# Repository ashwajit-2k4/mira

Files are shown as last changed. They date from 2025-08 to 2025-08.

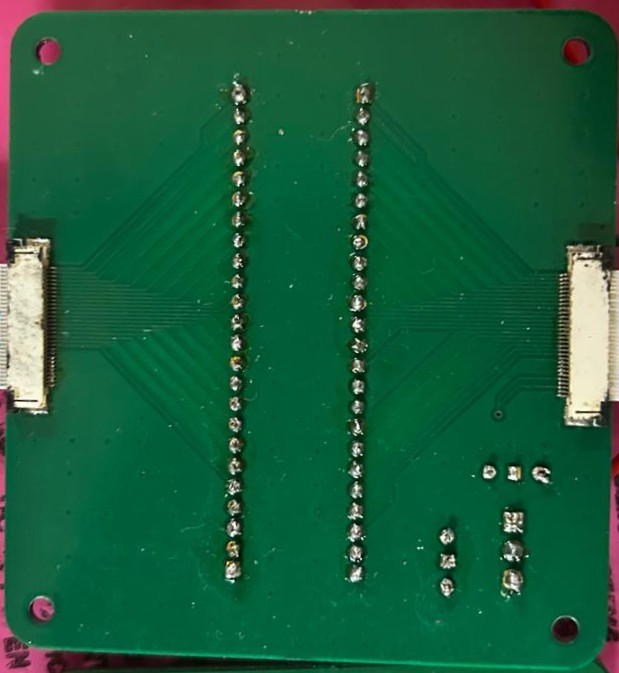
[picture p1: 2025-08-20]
pcb/PCB_2/pictures/CMOD_PCB_Back_Assembled.jpeg

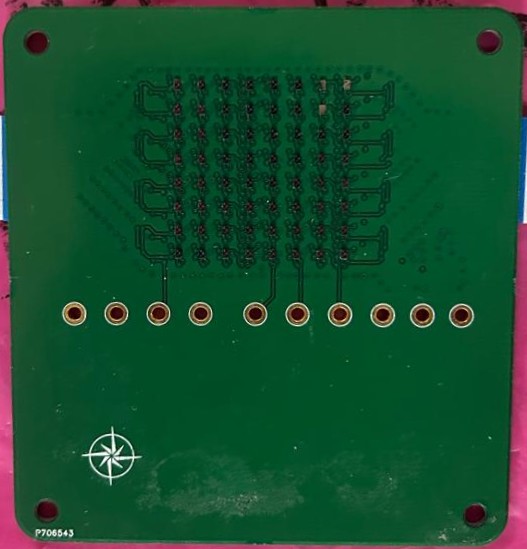
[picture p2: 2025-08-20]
pcb/PCB_1/pictures/EDL_3001_PCB_Back_Assembled.jpeg

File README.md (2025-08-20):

### EDL 2025 Project Submission Repository.

### Project Name: P-05 : Magnetic Field Camera
### Team Number: MON-08
### Team Members:
- Aditya Vema Reddy Kesari (22b3985)
- Ashwajit Singh (22b1227)
- N V Navaneeth Rajesh (22b1215)
- Raunak Mukherjee (22b3955)
- Suchet Gopal (22b1814)

### Problem Statement and Solution:

<!-- Provide a description about the project and what you've learnt and achieved in this. -->

<b> Problem Statement </b> 

High resolution magnetic imaging of objects is extremely important in industrial applications, to check for defects in manufactured parts like permanent magnets or motors. However, many current products like MAGCAM have exhorbitant costs that make them unviable for many people.

<b> Our Solution </b> 

MIRA M1 fills in this gap, as an affordable  magnetic field camera consisting of an 8x8 sensor array, that maps the field distribution in the volume around an object using an r-theta-z movement rig in just a few minutes. 

The object to be measured is placed on a rotating platform, with the sensor array itself moving in the r-z plane, thus enabling the mapping out of 3D space. The user interacts with a laptop-based GUI, to move the sensors to the starting position, and then start the pre-programmed sweep. The GUI then shows the live heatmap of the values the sensor array sees (at above 80 frames per second), along with a continuously updating scatter plot showing a 3D visualisation of the field.

<b> How It Works </b> 

The GUI starts an SSH connection to a Raspberry Pi, that controls the motors for rig movement, and communicates with the CMOD A7 FPGA that interfaces with the sensor array. When acquisition is started, the RPi rotates the theta motor by 360 degrees in 200 steps, acquiring data from sensors in every step. It then moves in the r direction in steps, repeating this process before it moves up in the z direction.

<b> Deliverables </b> 

- 2mm spatial resolution: **Achieved** (Currently with 1.75mm resolution, which can be increased further)
- 1mT sensitivity: **Achieved** (Obtained 0.2mT sensitivity)

### Key Learnings

Since our project had a lot of moving parts, with the CMOD FPGA, the Raspberry Pi microcontroller and the laptop GUI, in addition to the motor movement mechanism, communication was essential to ensure compatibility between these parts. Additionally, we had to put a lot of thought into component choice, since we could not use commonly available steel components due to interference. Since we required very high resolution, both in terms of magnetic field and spatial movement, it required careful design of PCBs and CAD models, and required adapting parts in the mechanism to ensure that we had minimum spatial error from jitter.

### Walkthrough of the repo

The source code consists of code for 3 devices: CMOD A7 FPGA, Raspberry Pi 5 and the laptop GUI. Additionally, the PCB designs for the sensor PCB we ultimately used, along with the backup PCB, and the PCB containing the FPGA are provided. The CAD models for all 3D printed and laser cut parts are also provided.

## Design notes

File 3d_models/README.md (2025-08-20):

# 3D Models

The project consists of several parts listed below. For further details please refer to the individual folders

1. **Large Spacer**: This design is used to hold the PCBs in place, connect to the sensor head and provide a point to attach the acrylic shields to protect the PCBs.

2. **Motor enclosure**: This holds the motor controlling the theta DOF (through the platform) using the 3D printed holder, and the motor bracket to attach the motor for controlling the radial DOF.

3. **Slider**: This part holds the entire z-axis movement mechanism. It slides along the radial direction, moving the entire sensor head, and holds the motor to move in the z direction.

4. **Sensor Head**: This holds the sensor and CMOD PCBs via the large spacer, and is connected to the threaded rod and the support rod controlling the z axis.

5. **CMOD Acrylic Shield**: This attaches to the large spacer and provides an enclosure for the CMOD board.

6. **Sensor PCB Shield**: This acrylic part provides an enclosure for the sensor PCB, and attaches to the large spacer.

7. **Small Spacer**: This part helps provide separation between the PCBs.

8. **Support Rod Holder**: This part simply holds the two horizontal support rods in place, and provides support to the other end of the threaded rod in the r-axis.

9. **Secondary Support Rod Holder**: This part holds only the support rods in place, with space in the middle to allow the motor shaft, coupler and threaded rod the pass through.

10. **Platform**: The object to be characterised is placed on this rotating platform.

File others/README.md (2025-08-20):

## Overview

The `others/` folder contains supplementary resources related to the final hardware assembly, usage, and documentation.

### Folder Structure

- **`PCBs/`**  
  Includes images of the fully assembled and soldered PCBs, along with a block diagram illustrating their interconnection and function in the system.

- **`Motors/`**  
  Contains photos of the perf board used for the motor driver circuit, including components and wiring.

- **`User Manual/`**  
  Provides a guide on how to use the project, including setup instructions, system overview, and basic operational steps.

---

These files serve as a reference for understanding the hardware integration and for guiding users on how to operate the magnetic field camera system.

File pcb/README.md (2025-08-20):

# PCB Overview

This folder contains all the design files, layouts, schematics, and assembled images for the PCBs developed for our project.

## PCB Summary

| PCB | Description | 
|-----|-------------|
| **PCB_1** | `TMAG3001 Sensor Array` – An 8×8 array using I2C-based TMAG3001 magnetometers. Used in the final sensor head. | 
| **PCB_2** | `CMOD Interface Board` – Interfaces the TMAG sensor array (PCB_1 or PCB_3) with a CMOD FPGA module. Includes power control and signal routing. | 
| **PCB_3** | `TMAG5170 Sensor Array` – A backup 8×8 sensor array using SPI-based TMAG5170 magnetometers. Fully compatible with PCB_2. | 

---

## Sensor Head Configuration

The **sensor head** for the magnetic field camera is built using:
- **PCB_2** (CMOD Interface)
- **Either** PCB_1 **or** PCB_3 (Sensor Array)

> Note: PCB_3 serves as an alternative to PCB_1 and can be used interchangeably without any hardware modifications.

---

## Manufacturing Note

Due to the complexity and design constraints, **none of the PCBs could be fabricated in-house at IIT Bombay**.  
All boards were professionally manufactured by **PCB Power**.

---

## Folder Contents

Each PCB folder contains:
- **Schematics**
- **PCB Layouts**
- **3D Renders**
- **Assembled Board Images**

---

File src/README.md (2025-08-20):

## Overview

This folder contains the complete codebase for the project, divided into three main components based on the hardware platform they run on:

### CMOD (FPGA)
- **Platform:** CMOD FPGA (e.g., CMOD A7)
- **Function:** Collects data from the TMAG sensor array and relays it to the Raspberry Pi via SPI.

### Raspberry Pi 5
- **Platform:** Raspberry Pi 5
- **Functions:**
  - Controls the motors and manages the motion of the sensor rig.
  - Receives sensor data from the FPGA and transmits it to the Laptop.

### Laptop
- **Platform:** PC or Laptop
- **Function:** Acts as the GUI for the project, providing visualization and user controls.

---

Each subfolder contains a more detailed description of the code and instructions on how to run it.

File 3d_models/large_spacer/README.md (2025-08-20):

# Large Spacer

## Purpose

This design is used to hold the PCBs in place, connect to the sensor head and provide a point to attach the acrylic shields to protect the PCBs.

##  Description

- **Type:** 3D print
- **Material Suggested:** PLA
- **Approx. Size:** 79mm x 80mm x 32mm

## Assembly Instructions

1. The two acrylic shields for the PCBs attach to either side of the part.
2. The PCBs are placed in between, with the extra space on one side for attaching to the sensor head
3. There are 4 3.2mm screw holes to attach parts together.
4. Please refer to the overall assembly image for reference

## Notes

A suggestion for future versions of this is to increase the clearance from the PCBs above, to allow space for the ribbon cables.

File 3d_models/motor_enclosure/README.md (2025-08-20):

# Motor Enclosure

## Purpose

This holds the motor controlling the theta DOF (through the platform) using the 3D printed holder, and the motor bracket to attach the motor for controlling the radial DOF.

##  Description

- **Type:** 3D print
- **Material Suggested:** PLA
- **Approx. Size:** 61mm x 57mm x 71mm

## Assembly Instructions

1. The 3D printed holder at the top allows the motor to be placed directly inside (an adhesive could be used for futher securing it)
2. The motor bracket is placed inside the enclosure, with the two slots fitting in. The motor is then screwed into it.

## Notes

The motors ran very hot, causing some bending in the plastic. A heat sink or a different material might be helpful.

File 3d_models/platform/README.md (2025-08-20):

# Platform

## Purpose

The object to be characterised is placed on this rotating platform.

##  Description

- **Type:** 3D print
- **Material Suggested:** PLA
- **Approx. Size:** 80mm x 80mm x 40mm
  
## Assembly Instructions

1. The 8mm shaft of the platform is inserted in the NEMA17 coupler, which in turn is connected to the motor controlling the theta DOF.

## Notes

A lnoger shaft for this piece would be better in a v2, since attaching it to the coupler was a struggle.

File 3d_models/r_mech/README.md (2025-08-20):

# Slider

## Purpose

This part holds the entire z-axis movement mechanism. It slides along the radial direction, moving the entire sensor head, and holds the motor to move in the z direction.

##  Description

- **Type:** 3D print
- **Material Suggested:** PLA
- **Approx. Size:** 65mm x 90mm x 50mm

## Assembly Instructions

1. 4 linear bearings are placed in the two holes on either side to run the support rods through
2. The flange nut is placed in the cavity in the centre hole, and a threaded rod is run through it
3. The motor controlling the z-axis is placed in the holder on top

## Notes

A suggestion for future versions of this is to increase the clearance from the PCBs above, to allow space for the ribbon cables.

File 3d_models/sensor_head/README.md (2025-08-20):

# Sensor Head

## Purpose

This holds the sensor and CMOD PCBs via the large spacer, and is connected to the threaded rod and the support rod controlling the z axis.

##  Description

- **Type:** 3D print
- **Material Suggested:** PLA
- **Approx. Size:** 40mm x 75mm x 70mm
  
## Assembly Instructions

1. 2 linear bearings are inserted in the 12mm hole to run the support rod through it.
2. The flange nut is inserted in the space provided with the screw holes, and the threaded rod is run through it.
3. This part is screwed to the spacers and PCBs through the screw holes provided.

## Notes

An additional nut would probably help with stability, or alternatively an additional support rod.

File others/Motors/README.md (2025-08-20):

### Motor Driver Connections  

We make use of 3 NEMA-17 stepper motors, one each for R, Theta and Z respectively. These are supplied power by the 12V SMPS (through the TB6600 motor drivers). The motor drivers make use of microstepping, and can be configured using the DIP Switches to change their current draw and microstep count.  

Since the motor driver inputs are differential, we connect one of +/- to GND and the other to a GPIO Pin of the RPi 5.

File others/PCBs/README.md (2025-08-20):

### PCB Descriptions  

The CMOD Interface PCB is connected the sensors by the means of 2x 30 pin FPC 0.5mm pitch connnectors, one on each side of the board respectively.  
The backside of the CMOD PCB faces the backside of the TMAG3001 PCB (i.e., the side with pullups and decoupling caps).   

The Screw terminal on the CMOD PCB is meant for power delivery to the CMOD via the 5V connection - this results in a current draw of < 100 mA in active mode. The 3.3V connection supplies the sensors and has a power draw of ~ 200 mA in active mode, ~ 23 mA in idle mode. The PMOD header connects the CMOD to the master readout device (in our case, an RPi 5).

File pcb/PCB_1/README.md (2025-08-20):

# TMAG3001 Sensor Array PCB

This repository contains the design files and documentation for the **TMAG3001 Sensor Array PCB**. This is the **main PCB** of the project, designed for high-resolution magnetic field sensing using a dense grid of magnetometers.

## Overview

- **Sensor Type**: TMAG3001 3-axis magnetometers  
- **Array Size**: 8x8 grid (64 sensors)  
- **Inter-sensor Spacing**: 3.5 mm  
- **PCB Type**: 4-layer board  
- **Communication Protocol**: I2C  

---

## Design Details

### I2C Bus Structure

Each group of **4 sensors** forms a **single I2C bus**.  
- Each **TMAG3001** uses **3 I2C lines**: `SCL`, `SDA`, and `INT`.
- A single bus handles 4 sensors, with address selection via the `ADD` pin.
- The `ADD` pin is tied to one of: `VCC`, `GND`, `SCL`, or `SDA` — enabling 4 unique addresses per bus.

> **Note**: To reduce the number of GPIOs, the `INT` lines from every **2 buses are shorted** together.

### Electrical Components

- **Pull-up Resistors**: 1.8 kΩ on all I2C lines  
- **Decoupling Capacitors**:
  - 0.1 µF per IC
  - 2 × 1 µF bulk capacitors at the power input  
- **Power Supply Pins** (per IC): `VCC`, `GND`, `INT`, `SCL`, `SDA`, `ADD`

### Physical Layout

- **IC Placement**: Only TMAG3001 ICs are placed on the **top** layer to avoid magnetic interference.
- **Other Components**: All resistors, capacitors, connectors, etc., are placed on the **bottom** layer.
- **Test Points**: 10 test points on the **bottom** for signal probing and ground testing.

### Grounding and Layer Design

- All 4 layers have **solid ground pours** for noise suppression and signal integrity.

---

## Files & Resources

The repository folders include:
- **Schematic**
- **PCB Layout**
- **3D Renders**
- **Assembled PCB Images**

---

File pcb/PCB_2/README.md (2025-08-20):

# CMOD Interface PCB

This PCB is designed to work in conjunction with the **TMAG3001 Sensor Array PCB**, forming a complete sensor head system. It serves as the interface between the microcontroller and the sensor array.

## Overview

- **Purpose**: Interface the TMAG3001 sensor array with a CMOD FPGA module  
- **CMOD Support**: Two sets of pin headers to securely mount the CMOD  
- **Signal Routing**: All signals are routed via ribbon cable connectors coming from the TMAG3001 Sensor Array PCB  
- **Power Supply**:  
  - Screw terminal block for providing power to both the FPGA and the sensor array  
  - Switches included to control the power supply to different sections

---

## Features

- **Ribbon Cable Connectors**:  
  - Located on both edges of the PCB  
  - Carry all signal lines from the sensor array PCB  

- **Power Interface**:  
  - Screw terminal for 3.3V/5V input  
  - Power control switches to selectively enable/disable supply to the FPGA and sensor PCB  

- **Mechanical Support**:  
  - Dual header slots to mount a CMOD A7 or similar FPGA board securely

---

## Files & Resources

The repository folders include:
- **Schematic**
- **PCB Layout**
- **3D Renders**
- **Assembled PCB Images**

---

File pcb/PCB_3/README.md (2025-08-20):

# TMAG5170 Sensor Array PCB

This PCB serves as a **backup** to the main TMAG3001-based board, utilizing **TMAG5170** sensors to form an 8×8 magnetometer array. It is a **2-layer** board designed for ease of hand assembly and SPI-based communication.

## Overview

- **Sensor Type**: TMAG5170 3-axis magnetometers  
- **Array Size**: 8×8 grid (64 sensors)  
- **Inter-sensor Spacing**: 4.625 mm  
- **PCB Type**: 2-layer board  
- **Communication Protocol**: SPI  

---

## Design Details

### SPI Bus Structure

Each **bus** handles 8 sensors (as seen in the schematic).  
- Required lines per bus: `INT`, `SCLK`, `MOSI`, `MISO`  
- Compatible with the same CMOD PCB interface used by the TMAG3001 board  
- Pins per TMAG5170 IC:
  - `VCC`, `GND`, `ALERT`, `SCLK`, `MOSI`, `MISO`, `TEST`, `CS`

> **Note**: Pin mapping ensures drop-in compatibility with existing CMOD interface hardware.

### Electrical Components

- **Pull-up Resistors**: 1.8 kΩ on all lines  
- **Decoupling Capacitors**:
  - 0.1 µF for each sensor IC  
  - 2 × 1 µF bulk capacitors at the input supply

### Physical Layout

- **IC Placement**: Only the TMAG5170 ICs are on the **front** of the PCB  
- **Other Components**: All resistors, capacitors, and connectors are on the **back**, minimizing interference during sensor operation   
- **Test Points**: 8 test points at the **bottom** of the PCB for signal and ground verification

### Assembly & Grounding

- Designed for **hand-soldering** – large enough component footprints  
- Both PCB layers are filled with **ground planes** for signal integrity

---

## Files & Resources

The repository folders include:
- **Schematic**
- **PCB Layout**
- **3D Renders**
- **Assembled PCB Images**

---

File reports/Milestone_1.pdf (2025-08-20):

# Project 5: Magnetic Field Camera

## MON-08

Aditya Vema
Ashwajit Singh
NV Navaneeth Rajesh
Raunak Mukherjee
Suchel Gopal

## Deliverable for Milestone 1

Please see forms that will be used for Milestone 1 evaluation. Two types of forms have to be filled out: 1. EE344_2025_milestone1 (1 form per team), 2. Individual_contribution_milestone1 (1 form per student)

You'll be asked to submit the following for Milestone 1 deadline (Feb 1st 2024):

1. PPT for Milestone 1, containing following information:
1. What is the problem that you are trying to solve?
2. Proposed solution, value proposition of your solution
3. How will you achieve the specifications? (i.e. overview of methodology, how did you arrive at the choice of solution after evaluating multiple options)
4. Technical details: principle of operation, target specifications, block diagram, justification of choice of components, BOM and accompanying circuit diagrams
5. Grant chart for project plan, work distribution across team members, week-wise goals
6. Key risks and mitigation strategies
7. Deliverables i.e. expected outcomes of the project
2. Video recording of PPT presentation (pre-recorded presentation. File size limit 100MB. Use Handbrake to compress video. Test your video and retake if needed)
3. BOM sheet (should be complete)
4. PDF of circuit diagrams of all blocks (as detailed as possible. BOM list should tally with circuit diagrams. Circuit diagrams may be hand-drawn using ruler and pen if that is more convenient and faster, but should be legible and all components should be clearly labeled.)

All the above deliverables have to be submitted for Milestone 1 deadline (Feb 1st 2024 - instructions and Google Form link will be shared)

## 01. Problem Statement

What is the problem we’re trying to solve?

- Quality control and manufacturing: Cracks, defects in permanent magnets used in motors, MRI machines
- Magnetic Shield Design and Testing: Helps design magnetic shields widely used in medical devices
- Medical Device Development: Testing implantable devices near magnets used in MRI machines
- Magnetic Levitation Systems: Testing bearings and components used in Maglev trains

## 02. Proposed Solution

What is the value proposition of our solution?
Millimeter precision and 3d interactive magnetic field visualisation to map the magnetic fields for crucial components in a short duration; enabling researchers to design and troubleshoot magnetic systems.

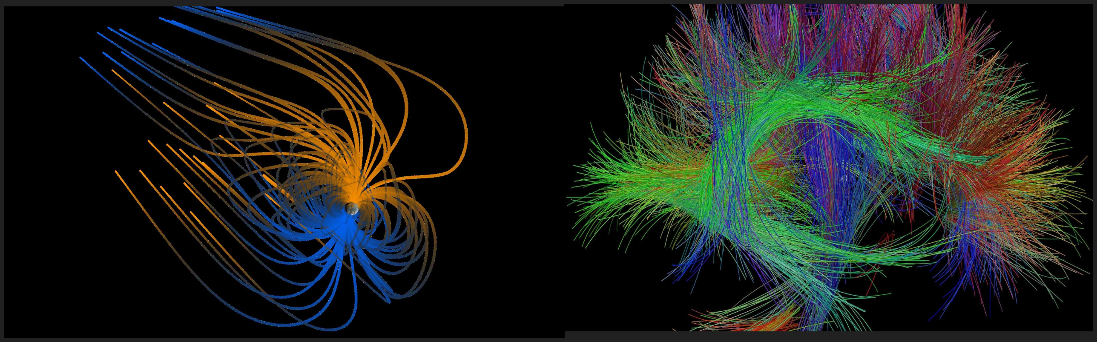
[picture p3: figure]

## 03. Achieving Specifications

How did we arrive at this solution after evaluating multiple options?

The alternatives have considerable drawbacks
1. Hand-held alternatives: Imprecise human operators require complicated sensors to detect position with no added benefit of precision
2. Magnetic Field with Real time Video: Real time video adds immense cost without the benefit of accuracy that is crucial to all conceivable applications.
3. Magnetic Field Cube: Our design facilitates 3 dof. We can thus repurpose several sensors to increase resolution in our measurement plane.
4. 2d field camera: Loses out crucial details present in the 3d magnetic field distribution

## 04. Technical Details

A. Principle of Operation
An 8x8 array of magnetic field sensors is mounted on an arm that moves cylindrically around an object and senses the magnetic field distribution all around. A microcontroller also keeps track of the position of the sensing arm and controls its motion accordingly.
An fpga also on the arm, acquires the readings from the sensors and sends it to a microcontroller which then sends it via wifi to a laptop. The laptop finally extrapolates the readings to generate a 3d interactive magnetic field distribution.

## 04. Technical Details

B. Target Specifications

## 04. Technical Details

C. Block Diagram

## 04. Technical Details

D. Justification of Components

## 04. Technical Details

E. Bill of Materials

## 04. Technical Details

F. Circuit Diagrams

## 05. Work Distribution

A. Gantt Chart

## 05. Work Distribution

B. Team work distribution

GUI Laptop - Vema
Sensor head
Physical layout, PCB (interface sensors, fpga) - Navaneeth FPGA coding - Suchet
Microcontroller Coding - Raunak
Prototyping Rig mechanism - Ashwajit

## 05. Work Distribution

C. Week-wise goals

## 06. Risks and Mitigations

A. Key Risks
1. Sensor Calibration: Each sensor has different sensitivities
2. Motor Calibration: Motors may be unreliable
3. Field Leakage: From motors

## 06. Risks and Mitigations

A. Mitigations
1. Sensor Calibration: Acquire standardised sensor as a baseline and compare measurements relative to this sensor
2. Motor Calibration: Trial and error; measure speeds
3. Field Leakage: Measure ambient field

## 07. Deliverables

What are the deliverables for our project?

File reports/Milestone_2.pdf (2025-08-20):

# Magnetic Field

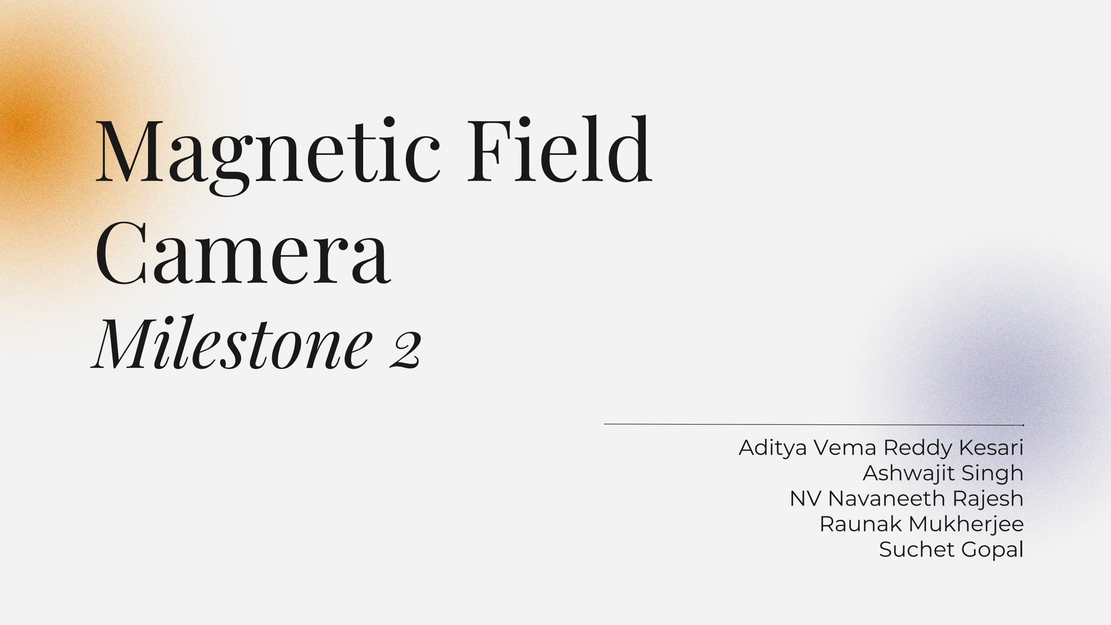
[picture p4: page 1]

# Camera

# Milestone 2

Aditya Vema Reddy Kesari
Ashwajit Singh
NV Navaneeth Rajesh
Raunak Mukherjee
Suchet Gopal

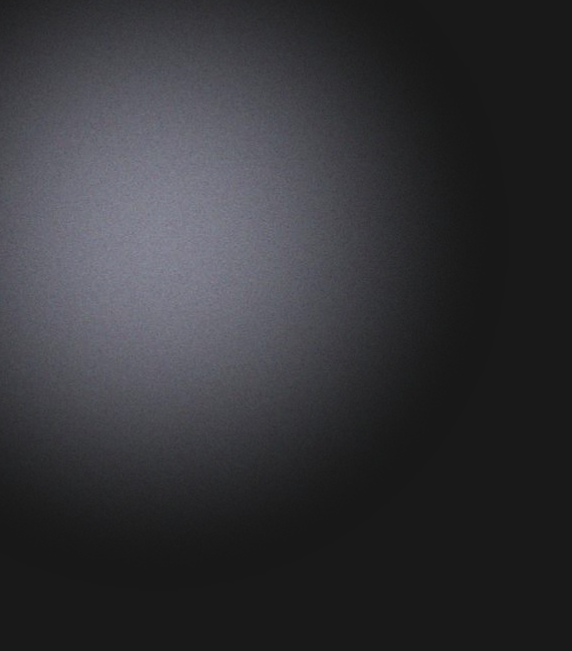
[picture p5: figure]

1.Feedback from milestone 1 Project management plan and documentation

2.

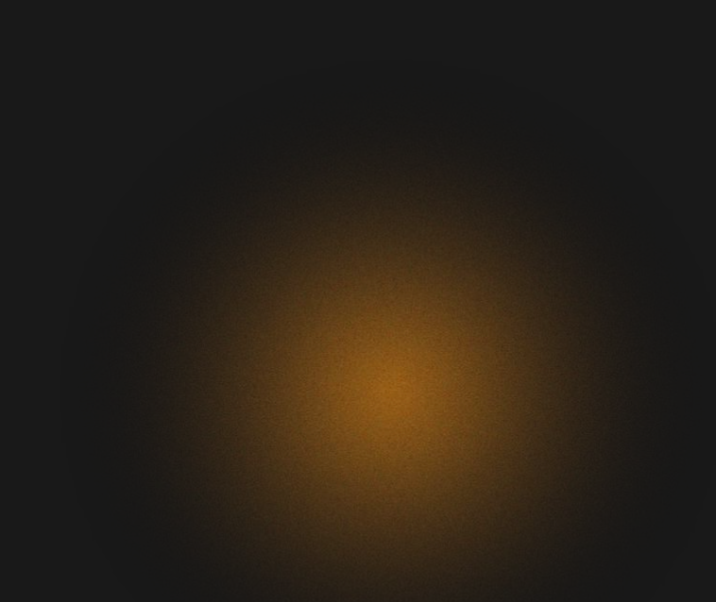
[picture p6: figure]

3.Progress updates
4.Block diagram and relevant analysis 5.Schematic and PCB layout 6.Preliminary tests and plan 7.Future plans

# Outline

# Feedback

01

# Feedback from Milestone 1

### Pictures of sensors

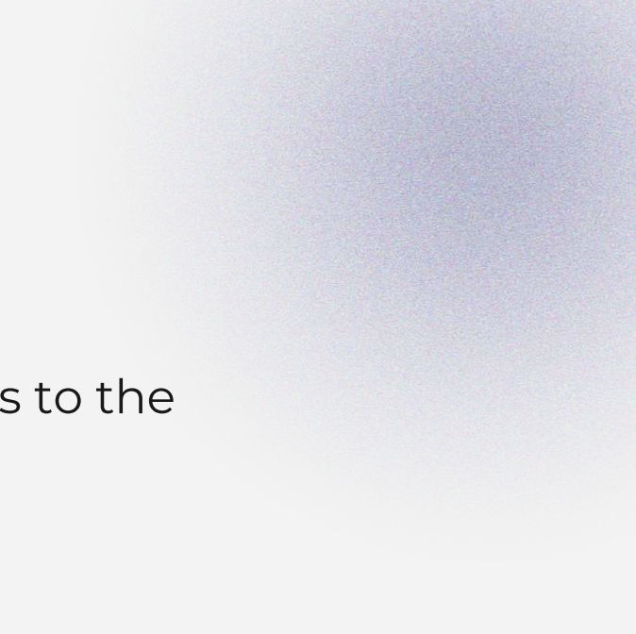
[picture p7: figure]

We added pictures of components to the presentation

### Component choice

We explored the reviewer’s suggestions, particularly for the FPGA, and settled on the current choice

### Clearer schematics

We created a hierarchy within the schematic and labelled nets for easier readability

# Project management

02

# Work Division

CAD and motor design: Designing the CAD files for the motor movement mechanism and the structure
Ashwajit, Raunak, Aditya
FPGA programming: VHDL for communication and data processing Ashwajit, Suchet
PCB Designing: Designing the TMAG3001 board, in addition to the breakout board for the alternate magnetometer
Navaneeth, Suchet

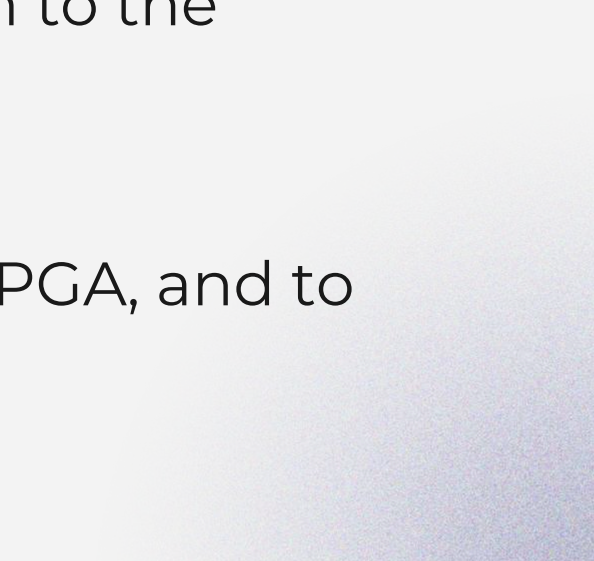
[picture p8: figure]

Microcontroller and GUI: Code to control the motors and FPGA, and to display the output on the laptop
Raunak, Aditya

# Documentation

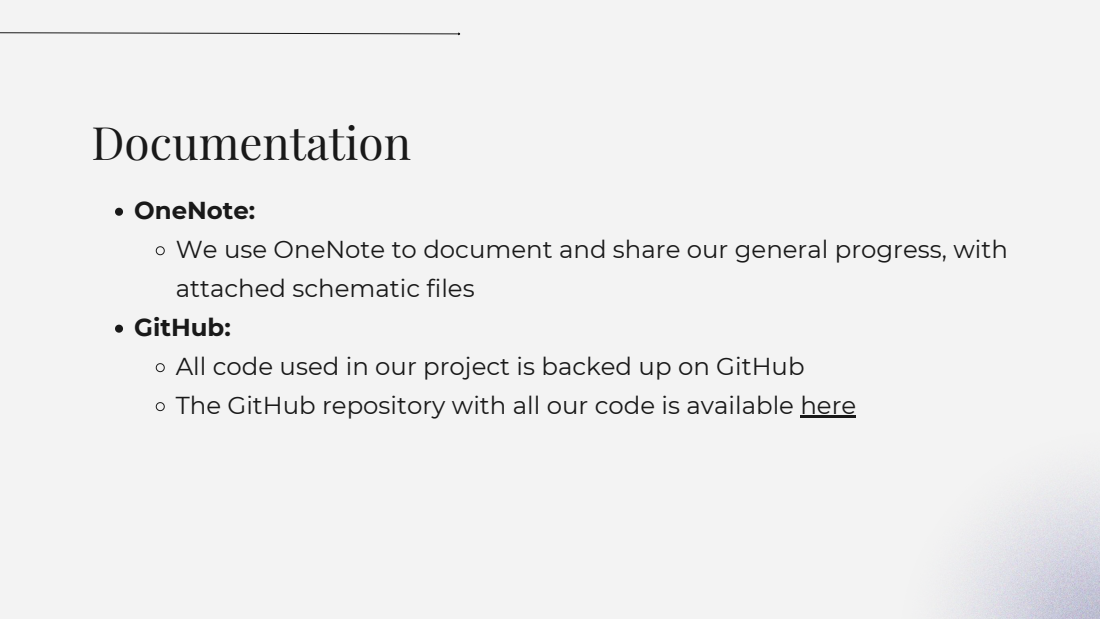
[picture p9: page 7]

OneNote:
We use OneNote to document and share our general progress, with
attached schematic files
GitHub:
All code used in our project is backed up on GitHub
The GitHub repository with all our code is available here (https://github.com/ashwajit-2k4/magneto)

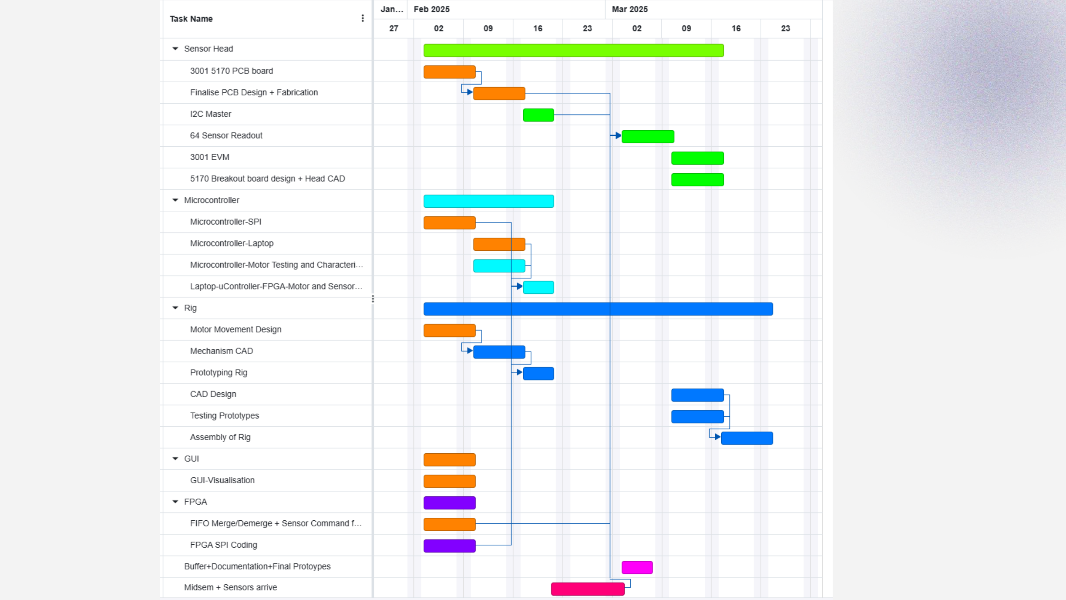
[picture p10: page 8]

# Deviations from original plan

The VHDL code for the I2C master and the SPI slave was delayed as iterating the PCB design took longer than originally expected
We could not test the functioning of the motor using the microcontroller due to non-arrival of parts
The CAD design is currently in progress, as finalising the top-level design of the mechanism took longer than expected

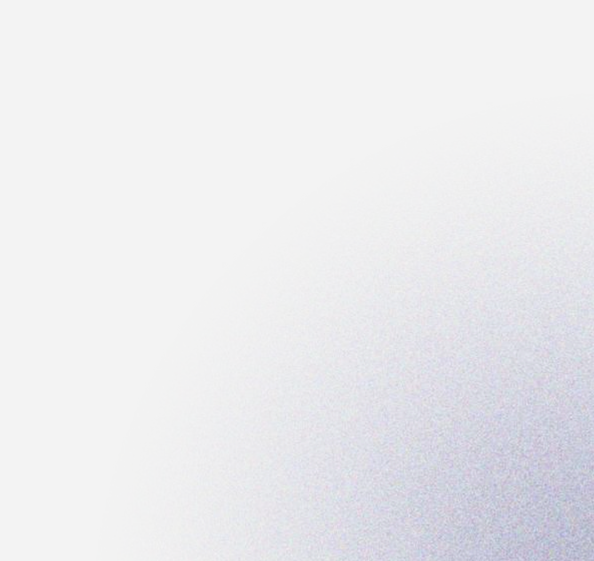
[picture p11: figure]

# Progress Updates

03

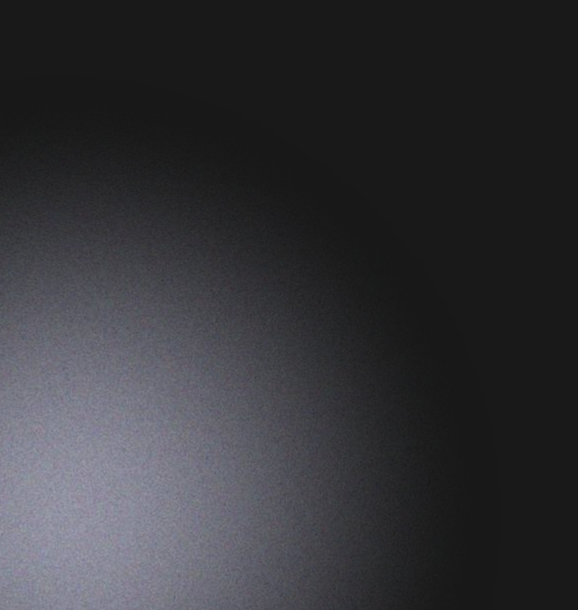
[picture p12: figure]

# PCB Design

TMAG3001 64 sensor array

Designed a high-density, four-layer PCB integrating a 64-sensor array of TMAG3001 magnetometers.
Developed a space-efficient layout for a 4-sensor I2C bus architecture to optimize signal integrity and maximize resolution. Carefully selected pull-up resistor values and decoupling

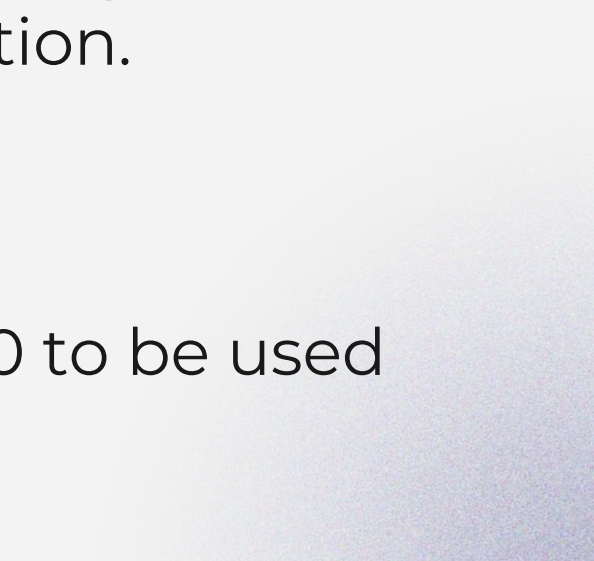
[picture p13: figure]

capacitor placements to ensure robust sensor operation.

TMAG5170 breakout board

Designed a breakout board consisting of 2 TMAG5170 to be used for testing of the sensors.

# Sensors Used

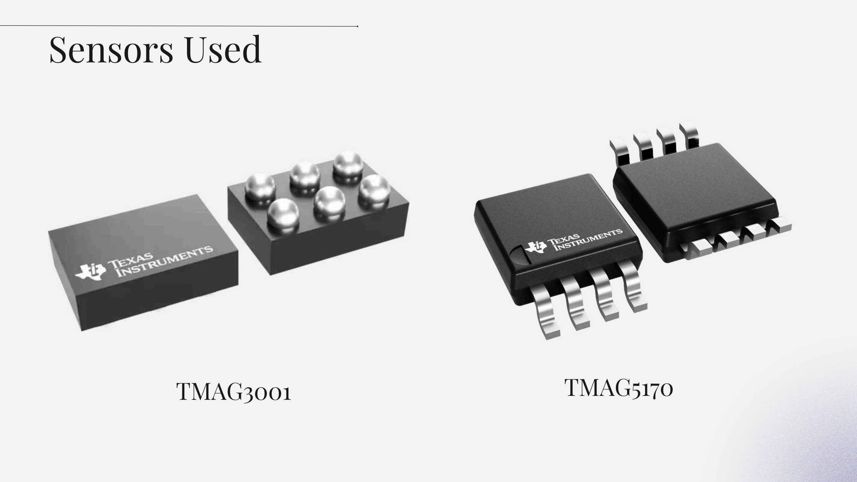
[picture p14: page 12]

TMAG3001 | TMAG5170

# FPGA Programming

The packet formats and communication protocol between the FPGA and the microcontroller were decided
The associated VHDL to unpack data from the sensor array and commands from the microcontroller and validate it were completed The code to add error detection and timestamps (to allow AC field detection) was also completed

# Microcontroller and GUI

The microcontroller SPI master was tested and was able to communicate with the CMOD-A7 FPGA
Additionally, the WiFi communication between the microcontroller and the laptop was tested
We finalised the GUI available on the laptop to visualise the fields

# Rig Design

Mechanism
We are continuing with the r-theta-z coordinate system to move the sensor head, since most
The sensor head will face in the theta direction as this allows us to cover the maximum area, since the theta-controlling motor will be moving the fastest

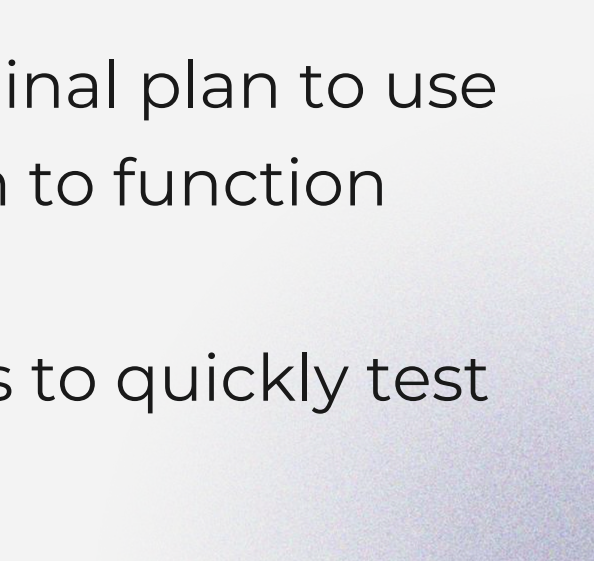
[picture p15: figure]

We are also using linear actuators instead of our original plan to use belts, as they require precise control over the tension to function Materials
The initial prototype will be 3D printed, as it allows us to quickly test the design, and does not interfere magnetically

# Rig Design

Materials
The initial prototype is 3D printed, as it allows us to quickly test the design, and does not interfere magnetically
We will be using nylon rods for support, as they are standard and will not interfere, and are planning to 3D print and laser cut custom linear actuators

# Block Diagrams

04

# Overall block diagram

# FPGA Code Structure

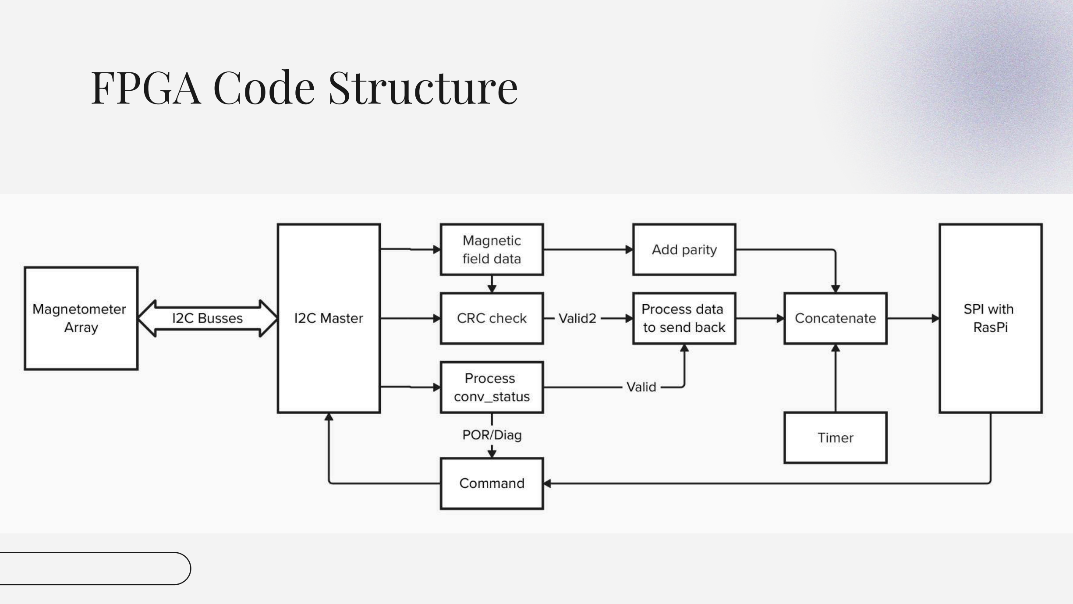
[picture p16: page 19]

# Schematics

05

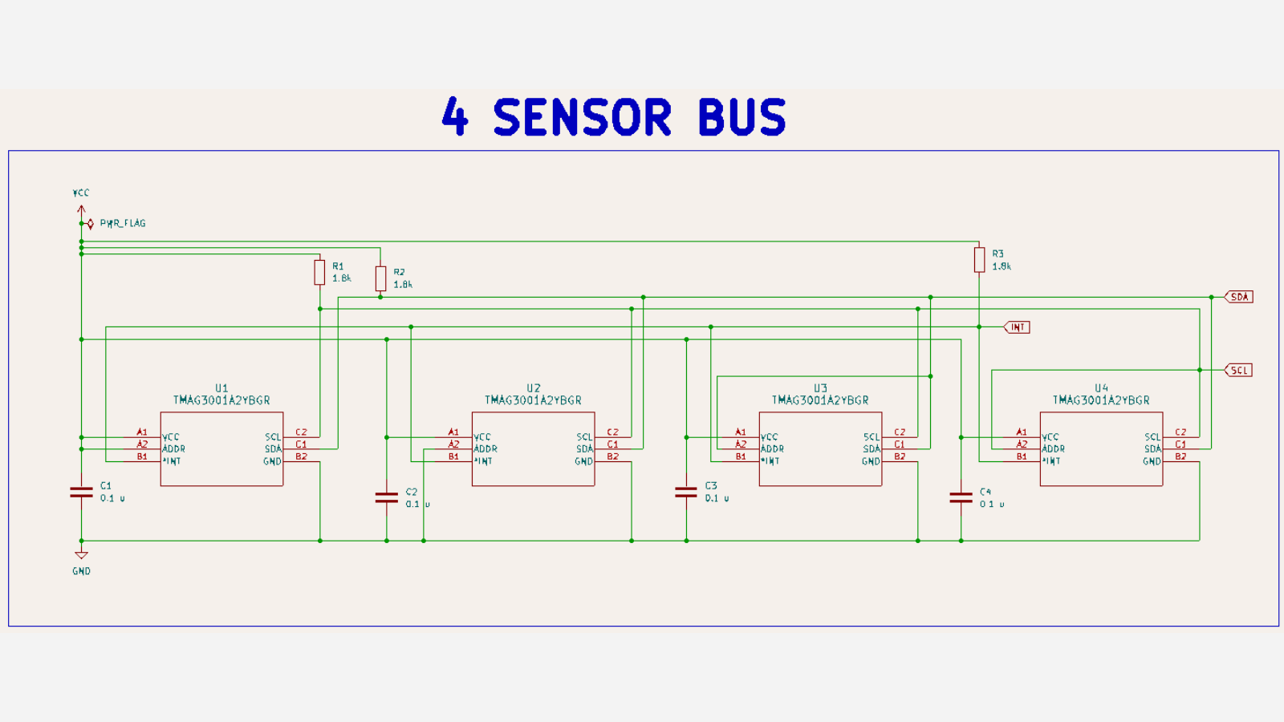
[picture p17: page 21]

### Pictures of sensors

We added pictures of components to the presentation

### Component choice

We explored the reviewer’s suggestions, particularly for the FPGA, and settled on the current choice

### Clearer schematics

We created a hierarchy within the schematic and labelled nets for easier readability

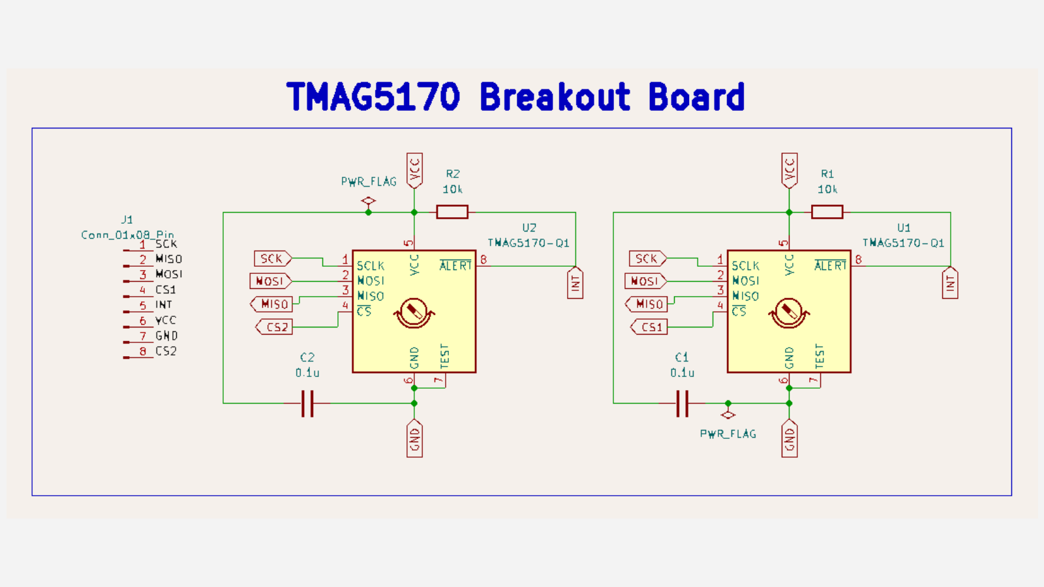
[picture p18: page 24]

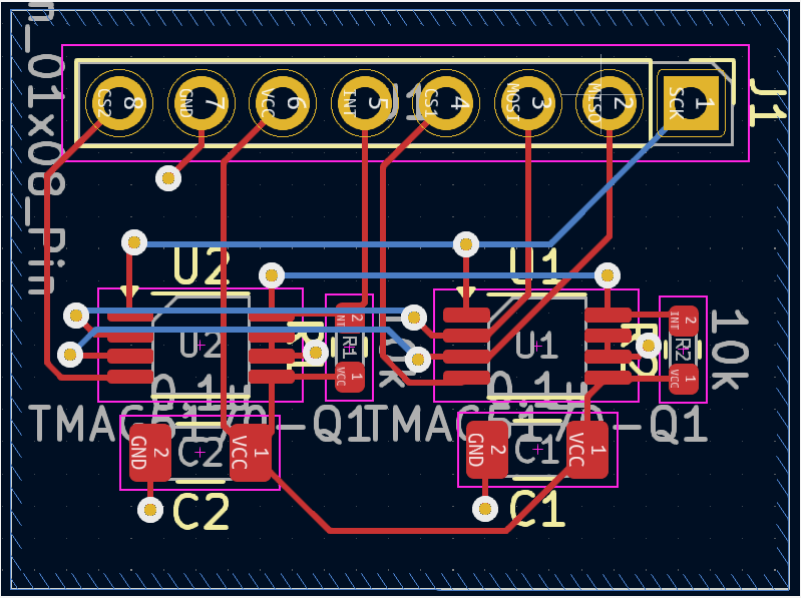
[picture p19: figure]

## FPGA-Sensor Bridge Schematic

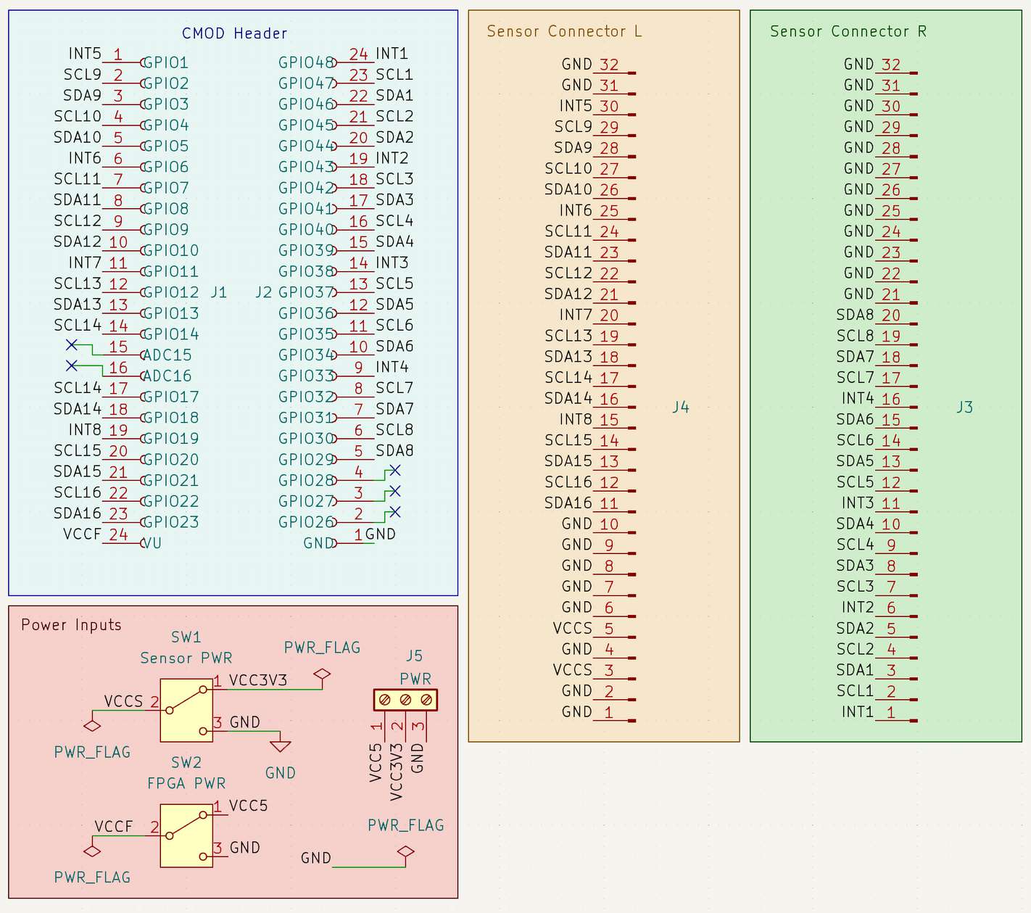
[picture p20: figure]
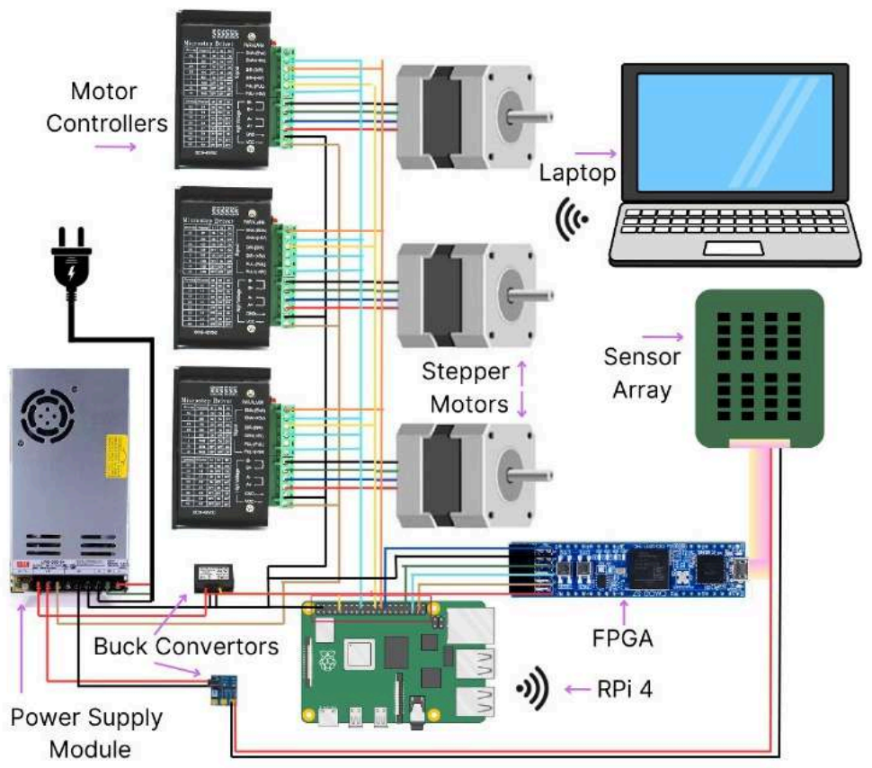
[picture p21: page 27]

# Preliminary Tests

06

# TI Simulation

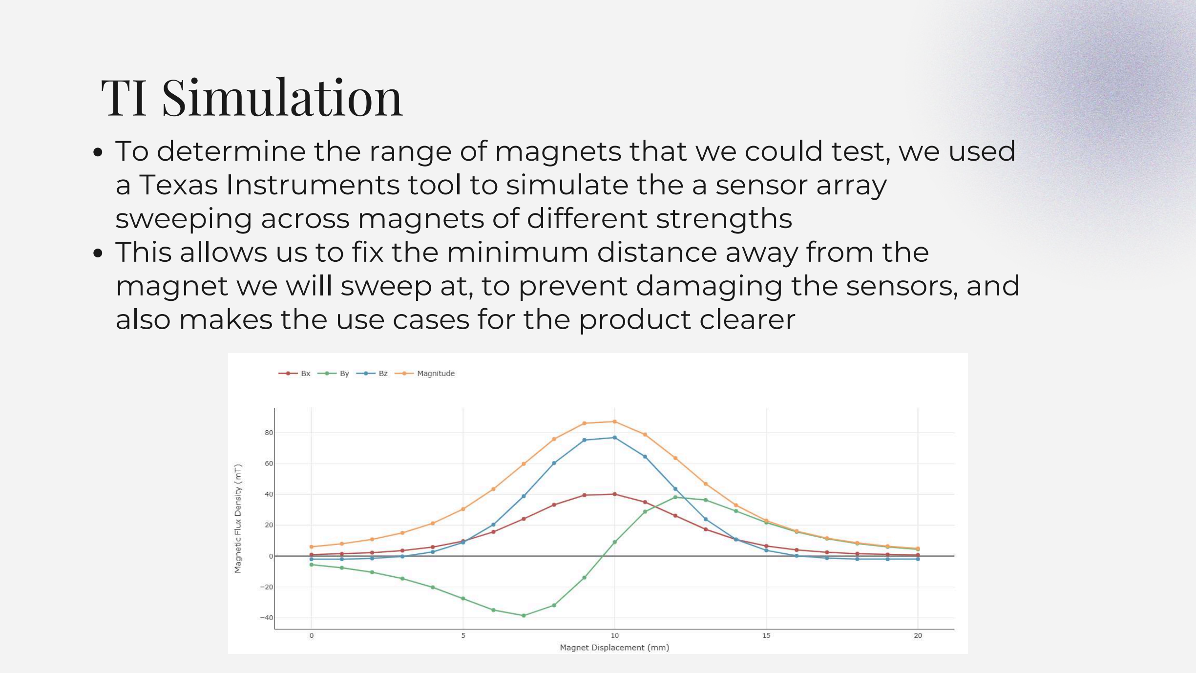
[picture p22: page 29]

To determine the range of magnets that we could test, we used a Texas Instruments tool to simulate the a sensor array sweeping across magnets of different strengths
This allows us to fix the minimum distance away from the magnet we will sweep at, to prevent damaging the sensors, and also makes the use cases for the product clearer

# FPGA-uC SPI

### Setup

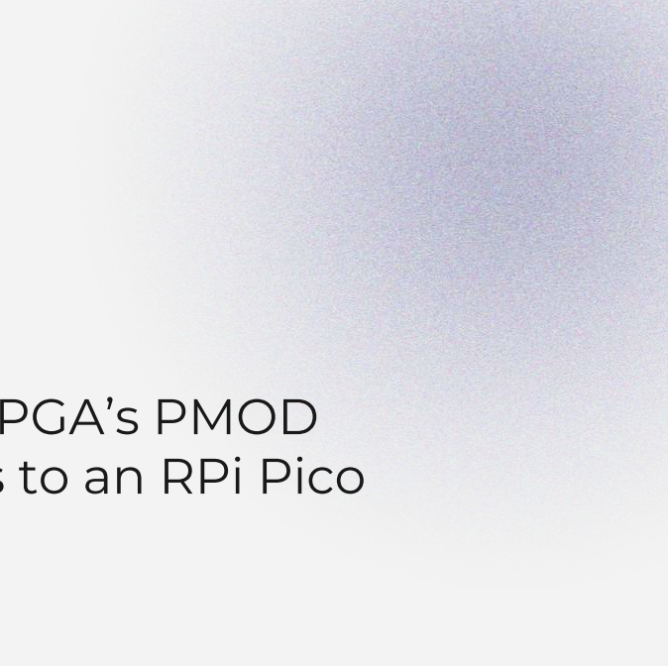
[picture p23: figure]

We made connections from the FPGA’s PMOD header using simple jumper wires to an RPi Pico

### Speed

We were successfully able to test SPI Communication up to 12 MHz, which is above spec.

### Software Delay

We have a software delay of about 60us per 128 bits using MicroPython, which is within spec. This can be further reduced using C++ if necessary.

# WiFi Test

### Connection

### Data Transfer

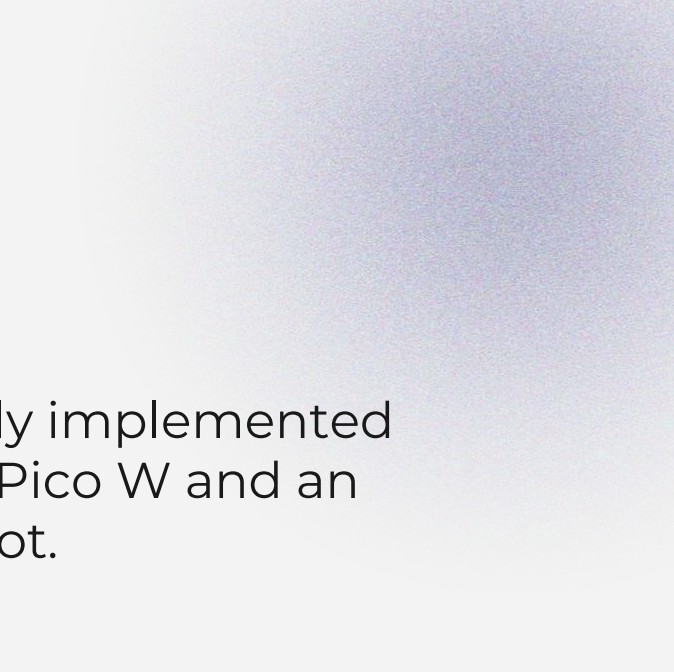
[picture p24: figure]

A WiFi connection was successfully implemented and tested using an Raspberry Pi Pico W and an Asus laptop over a supplied hotspot.

Data was then sent from the Raspberry Pi Pico W to the laptop using Internet Protocol. The data sent was a basic html page that was received and correctly displayed on the laptop demonstrating real time transfer capabilities.

# GUI Test

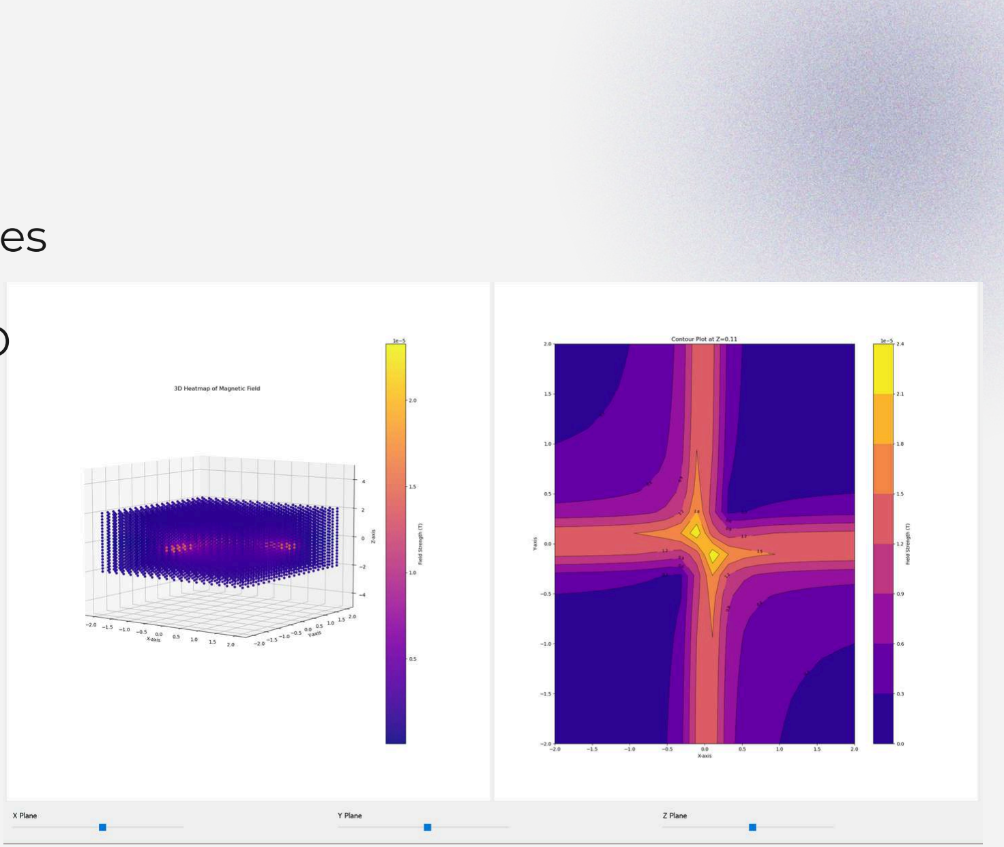
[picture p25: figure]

Implemented several techniques of visualisation available on matplotlib including 2D and 3D quiver plots, heat maps and contour plots.
Finalised the design to be a 3D zoomable and rotatable heat map along with a 2D heat map of any plane specified by user Aim to implement a 2D heat map cum quiver plot of the plane parellel to the current orientation of the 3D heat map as default

# Future Plans

07

# Mechanical Design

We prioritised electronic design initially to ensure we could send our PCBs for printing as soon as possible
The priority in the near future is to focus on mechanical design, and create an initial 3D printed prototype to test the accuracy of the linear actuators and rigidity of the design
We aim to complete and test the first prototype in the first week of March
Following this, we will place an order for the necessary mechanical components and build the final version

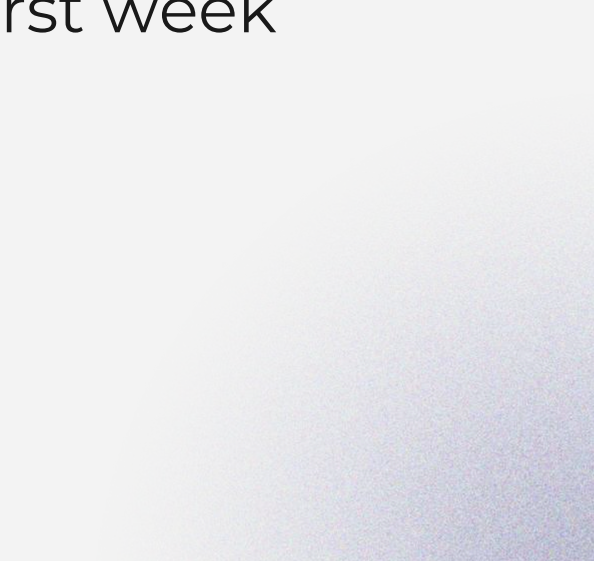
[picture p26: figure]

# Motor testing

We initially planned to test the motors and their accuracy this week, but due to a delay in procuring the components we were unable to
This is a priority as it determines the resolution of our camera, and the microcontroller code will have to be tweaked accordingly


Getting a better idea of the dimensions also allows us to design the case for the motors

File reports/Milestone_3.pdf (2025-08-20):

# Magnetic Field


# Camera

# Milestone 3

Aditya Vema Reddy Kesari
Ashwajit Singh
NV Navaneeth Rajesh
Raunak Mukherjee
Suchet Gopal

1.Feedback from milestone 2 2.Progress updates
3.Proof of concept/ Block Diagrams 4.PCB


5.CAD Design and Power management 6.Critical Tasks and Key Risks
7.Future plans


# Outline

# Feedback

01

## Feedback

Pictures of sensors

We added pictures of components to the presentation

Component choice

We explored the reviewer’s suggestions, particularly for the FPGA, and settled on the current choice

Clearer schematics

We created a hierarchy within the schematic and labelled nets for easier readability

# Progress Updates

02


## CAD design

Progress :
We have a complete CAD design, and will receive approval for 3D printing this week
We had to make changes to our initial design ensure the weight of the motors could be supported by our 3D printed parts
We still employ an r-theta-z system, but changed the positioning of the motors to ensure a more stable design


## Breakout board


Progress :
Unfortunately we received the breakout board much later than expected (earlier this week) so we have not had time to debug our I2C interface from the FPGA to the sensor.
This is not a very complicated task and should be done by next week.
We will also have our sensor PCB back from assembly by next week to compare with the breakout board testing results.

## Rig movement (Motors)


Progress :
Tested motor for multiple runs to check for cumulative error. Observed < 5 degree error thus concluding that the error is non cumulative.
Measured time per step for each microstep.

## GUI Design

Implemented several techniques of visualisation available on matplotlib including 2D and 3D quiver plots, heat maps and contour plots.
Finalised the design to be a 3D zoomable and rotatable heat map along with a 2D heat map
of any plane specified by user
Aim to implement a 2D heat map cum quiver plot of the plane

parellel to the current orientation of the 3D heat map as default Also developed a web page instead of a window to improve speed of interface

## Deviations from original plan

We made changes to the initial CAD design after receiving and testing the motors, to ensure that it is more stable

Obtaining steady SPI readout between the RPi and the CMOD A7 took longer than expected, as it was often very erratic

Testing of TMAG3001 sensors delayed due to delayed arrival of the breakout board


# Proof of concept/


# Block Diagrams

03

## Overall block diagram

## Working Demo Motor


## Working Demo of GUI (Window)

## Working Demo of GUI (Web)


# PCB

04

## Updates


Three PCBs submitted for fabrication from PCB Power
TMAG3001 Sensor Array PCB
CMOD Board PCB
TMAG5170 Sensor Array PCB
TMAG3001 and CMOD PCBs Gerber files approved by PCB power
and fabricated, to be assembled next week.
TMAG5170 Gerbers to be approved by PCB power.
Stage 2 cleared and external vendor recommended for all PCBs


## TMAG3001 PCB

## CMOD PCB


## TMAG5170 PCB

## Key Learnings

The TMAG3001 magnetometer is very small (0.8×1.3 mm), which led to a few issues and learnings.

Necessitated using similarly sized resistors and capacitors to minimize space usage. (0402 footprint)

Due to the small size, it cannot be hand-soldered.

The usual 0.2 mm track width is insufficient for connections due to the close pin spacing on the IC, requiring a smaller track width and clearance. (0.18 mm chosen)

## Key Learnings

A 2x2 layout for the PCBs was initially chosen but later we realized that the routing became complicated and switched to a linear design.

The design evolved from a 2-layer to a 4-layer PCB to manage signals more efficiently and allow for closer spacing between the sensors.

The SDA and SCL lines were kept in the same plane to minimize capacitance issues.

Two power sources were used to ensure that the current limit of the ribbon cable (0.5 A) was not exceeded.

## Choices made and Justification

The TMAG3001 was preferred due to its smaller size, allowing for higher resolution and I2C interfacing, which is more suitable for the array design.

Adopting a 4-layer design helped in managing the complex routing required, reducing clutter and improving signal integrity.

TMAG5170 was chosen as our backup sensor as it uses SPI in which we have more experience. It is larger in size, allowing robust fabrication.

We chose an external vendor as the IITB lab constraints were too large for either of our sensor PCBs.

## Design Evolution


## Final PCBs

TMAG3001 PCB | TMAG5170 PCB

## Final PCBs


CMOD PCB

# CAD Design and


# Power management

05

## CAD Design

Our CAD design got delayed beyond the last milestone since we received the motors late
On testing the motors, we found that while they could support a high torque, supporting their weight on a moving platform could be difficult
Our new design has all motors’ weight supported by the base The design to enable movement of the arms in the r and z direction uses a threaded rod instead of rubber belts (like in traditional 3D printers) to ensure higher accuracy, since ensuring appropriate slack on a prototype is difficult
We were unable to get it reviewed this week, but will do so in the lab on Monday

## Overall Design


## Theta movement

## R movement


## Z movement


## Components to be 3D printed


Sensor Head | Platform | Base
Track | Motor adapter

## Power Management

We have a single 12 V SMPS that we use to provide power to the microcontroller, the FPGA, the sensors and the motor drivers These components require 12V, 5V and 3.3V supplies which we provide using buck converters
While there are individual buck converters that can provide both 5V and 3.3V, they did not meet our current requirement for the sensor, so we use two separate converters


# Critical Taks and


# Key Risks

06

## Critical Tasks

Testing the breakout board with the I2C master


3D printing the required components, and testing the motor movement with the entire assembled rig to ensure we have millimetre accuracy

Testing 64 sensor readout to the CMOD FPGA on receiving the PCB

Testing the power management system with the whole system to ensure it meets current requirements

## Key risks

The passive heat dissipation of the motors is insufficient Solution: We have found heat sinks, fans and an adapter to connect them to the motor if required. The CAD is designed such that it can easily be adapted to this if required
The sensor PCB does not function as expected Solution: We have a 64 sensor array with 16 buses, so one bus being affected still ensures we can obtain a map of the field. If the PCB as a whole does not work, we have a second PCB with a different sensor that we can use instead
The rig movement is not accurate enough Solution: We have motor drivers that allow for microsteps for higher resolution. We also have proximity sensors that can be used to calibrate position before a run

# Future Plans

07

Aditya: Fine-tuning GUI and adding ability to control the system from the laptop
Raunak: Completing integration of microcontroller code to allow control of all components simultaneously
Ashwajit: Printing and assembling the rig and testing accuracy of movement, and making changes for heat management
Suchet: Further breakout board testing, FPGA code for 64 sensors and readout to RPi
Navaneeth: Solder work for PCBs, Testing readout of 64 sensor PCB, Interfacing sensor data with GUI.

## Work Distribution until Final Demo

## Plan for Final Demo

Once the power supply is turned on, all the components are powered, but they are controlled from the laptop GUI via the microcontroller
We first send a command to do a sweep across the volume to note the background magnetic field
We then place a motor or a permanent magnet on the platform to find the magnetic field generated by it
This is sent back to the laptop via WiFi, and shown in the GUI as in a previous slide
A stretch goal is to be able to show periodic magnetic fields like from AC current, which the sensors have the capacity to do

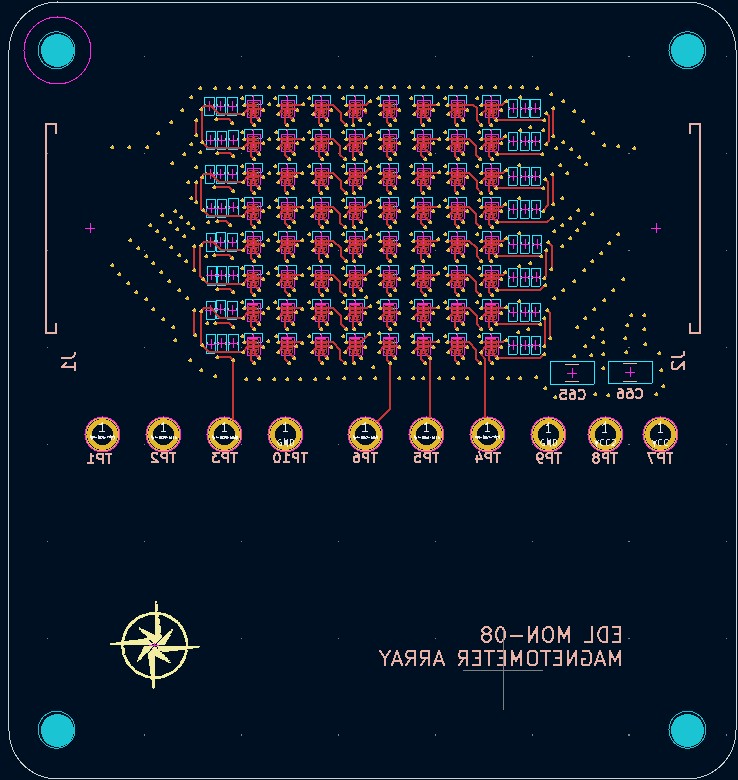
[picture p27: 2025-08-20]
pcb/PCB_1/pictures/EDL_3001_Layout_Front.jpg

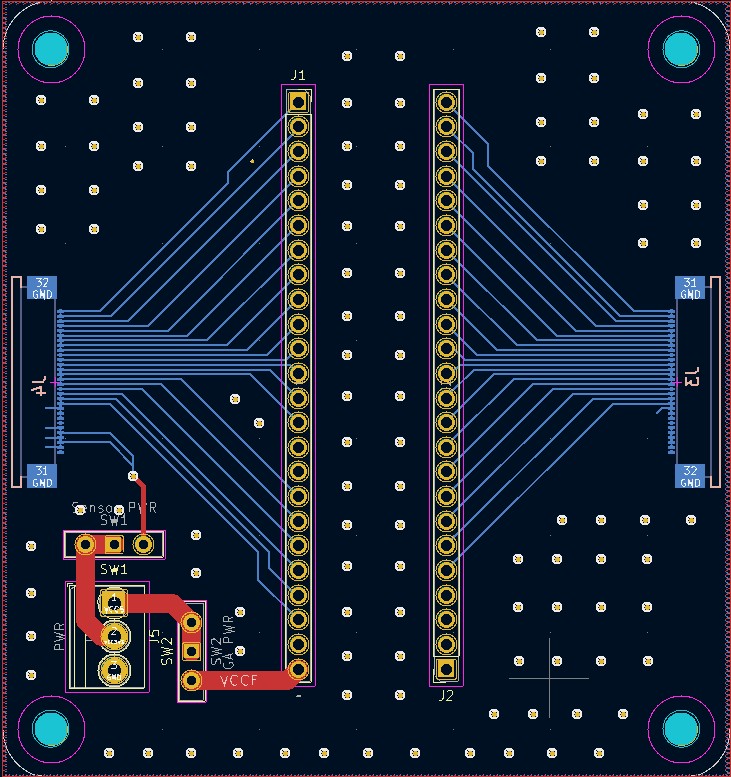
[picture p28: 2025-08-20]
pcb/PCB_2/pictures/CMOD_Layout.jpg

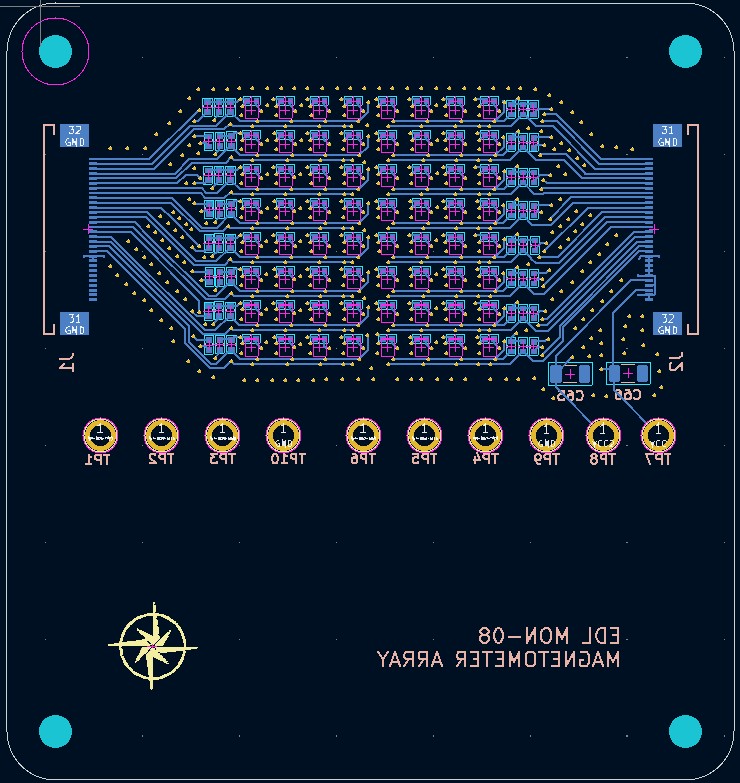
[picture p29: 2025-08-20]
pcb/PCB_1/pictures/EDL_3001_Layout_Back.jpg

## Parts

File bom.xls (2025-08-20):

Project Title: Magnetic Field Camera
Group ID: MON-08
Name of the Group Member/s: Ashwajit Singh, Suchet Gopal, Raunak Mukherjee, NV Navaneeth Rajesh, Aditya Vema Reddy Kesari
Component Name | Type | Quantity | Part Number | Manufacturer/Vendor | Cost | Description
CMOD A7-35T | Module | 1 | CMOD A7-35T | WEL (Digilent) | 12412.46 | FPGA
TMAG3001 | IC | 80 | TMAG3001A2YGBR | Digikey | 3914.59 | Magnetometer
Raspberry Pi | Module | 1 | Raspberry Pi 5 | WEL (Raspberry Pi) | 8209 | Microcontroller
NEMA 17 | Actuator | 3 | JK42HS60-1206F NEMA17 | Robu | 2937 | Stepper Motor
TB6600 motor driver | Module | 3 | TB6600 | Robu | 1197 | Motor Driver
SMPS | Module | 1 | ME-12V10A-MS | WEL (METEK) | 500 | Power Supply
Capacitors | Consumables | 98 | 0402X104K160CT | Multicomp Pro | 83.5 | 0.1 uF SMD 0402 Capacitors
Resistors | Consumables | 105 | R46KF310040POM | KOA | 115.5 | 1.8 k SMD 0402 Resistors
Connector | Consumables | 2 | 52435-3071 | Molex | 337.3 | FFC/FPC Ribbon Cable Connector
Flexible coupler | Consumables | 1 | NEMA17 5mmx8mm | Robu | 99 | Flexible aluminium coupler for helical shaft
Rigid coupler | Consumables | 2 | NEMA17 Shaft Coupling 5mm X 8mm | Robu | 198 | Rigid aluminium coupler for helical shaft
Screw terminal | Consumables | 1 | XY302V 3.5mm pitch | Robu | 12 | 3.5 mm pitch screw terminal
Threaded Rod | Consumables | 2 | SS304 Threaded Rod + Brass Nut | Amazon | 490 | 300 mm length, 8mm diameter threaded rod with brass nut
Switches | Consumables | 2 | SS-12D10G3-Slide 1P2T Straight Switch | WEL (Robu) | 34 | 3mm pitch SPDT switch
Ribbon Cables | Consumables | 2 | 547317 | Robu | 66.1 | 0.5 mm pitch 30 pin 200mm FPC A-type Ribbon flexible flat cable
Jumper wires | Consumables | 100 | - | Robu | 250 | 10 CM Dupont Cable Male/Male, Male/Female, Female/Female Cable Combo
Linear ball bearing | Consumables | 6 | LM8UU 8mm | Amazon | 780 | 8mm Linear Ball Bearing Bush Steel
Motor bracket | Consumables | 1 | Mounting L bracket | Amazon | 299 | Mounting L Bracket of NEMA 17 Stepper/Stepping Motor
Smooth Rod | Consumables | 3 | EN31 | Amazon | 525 | EN31 Steel Smooth Rod 8mm OD 300mm (0.3 mtr)
Voltage regulator | IC | 1 | L7805CV | WEL (Robu) | 22 | Linear Voltage Regulator, 7805, Fixed, Positive, 10V To 35V In, 5V And 1.5A Out
Capacitors | Consumables | 16 | C1206C105K1RACTU | WEL (KEMET) | 96 | 1 uF SMD 1206 Capacitors
CMOD PCB | PCB | 2 | - | Power PCB | 3021 | -
TMAG3001 PCB | PCB | 2 | - | Power PCB | 5468 | -
TMAG3001 PCB Assembly | PCB | 1 | - | Power PCB | 9873 | -

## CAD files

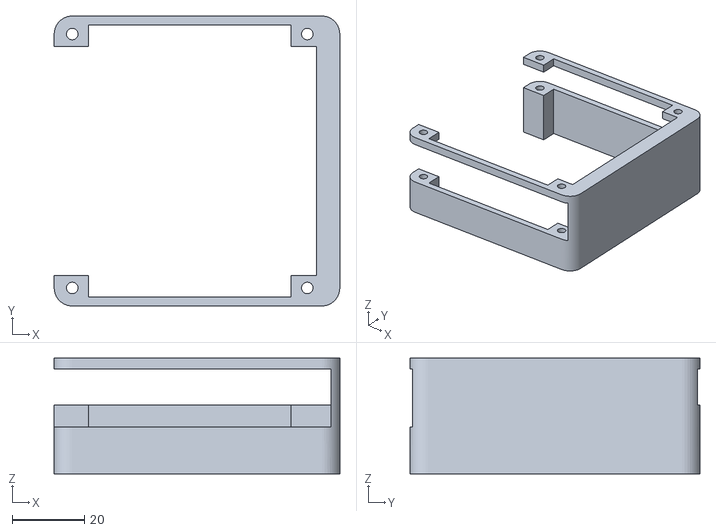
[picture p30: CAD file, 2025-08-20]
3d_models/large_spacer/model.stl
79.0 x 80.2 x 32.0

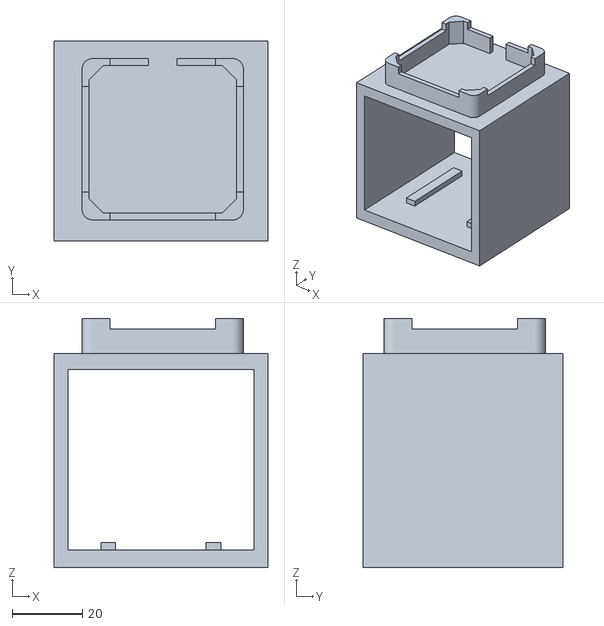
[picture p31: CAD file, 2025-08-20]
3d_models/motor_enclosure/model.stl
61.0 x 57.0 x 71.0

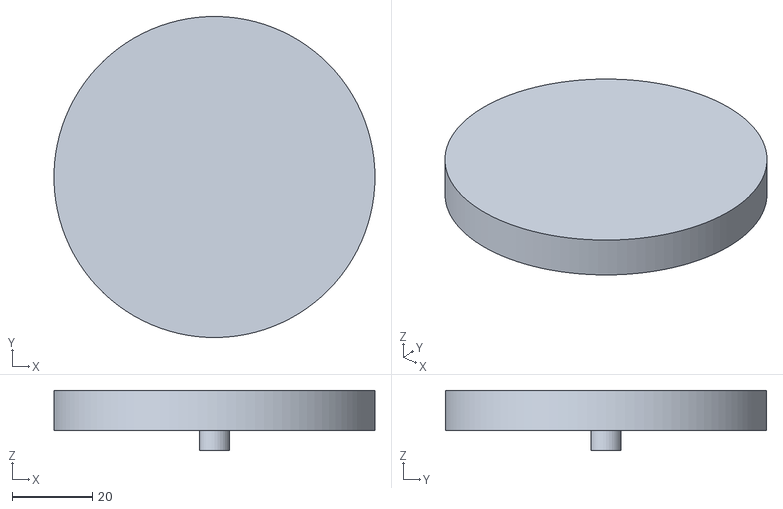
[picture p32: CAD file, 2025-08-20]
3d_models/platform/model.stl
80.0 x 80.0 x 15.0

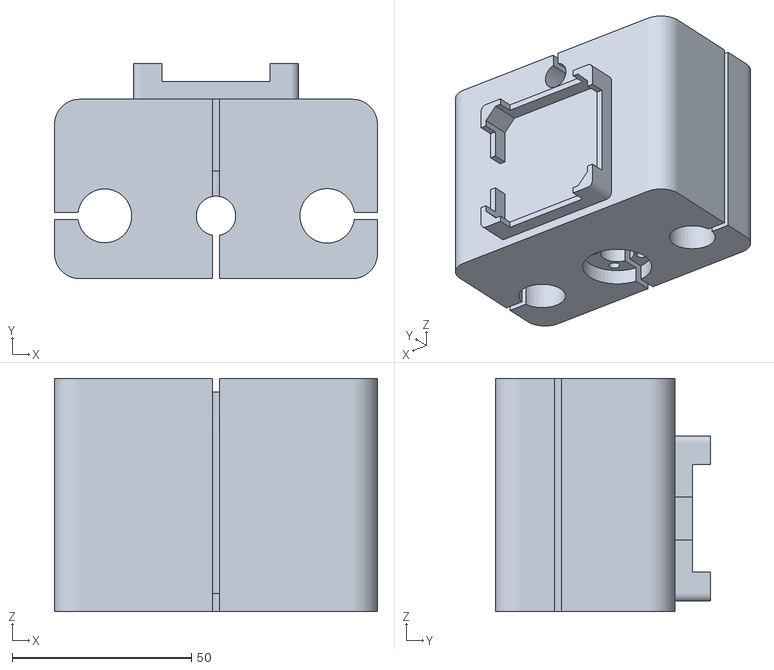
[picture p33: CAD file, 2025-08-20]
3d_models/r_mech/model.stl
90.0 x 60.0 x 65.0

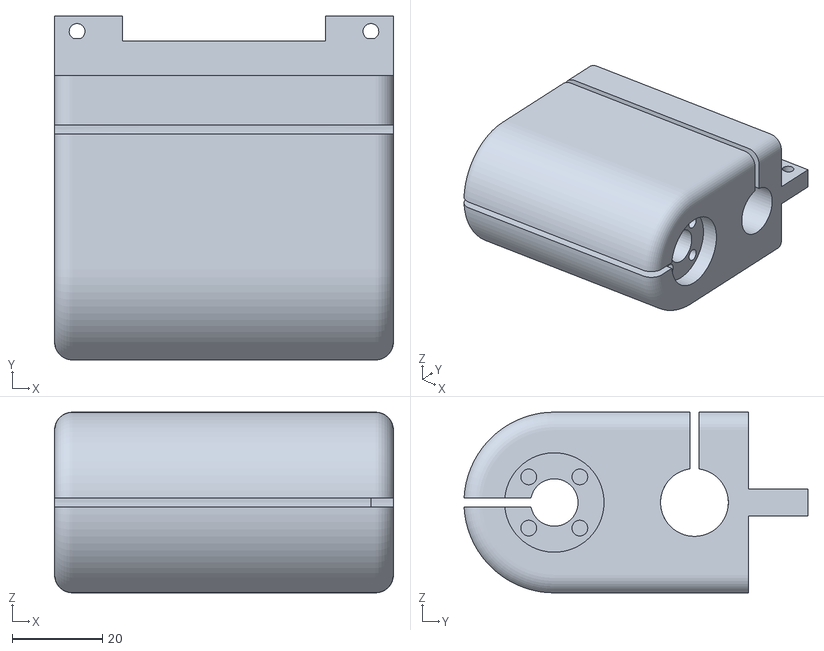
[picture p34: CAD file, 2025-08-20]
3d_models/sensor_head/model.stl
75.0 x 76.1 x 40.0

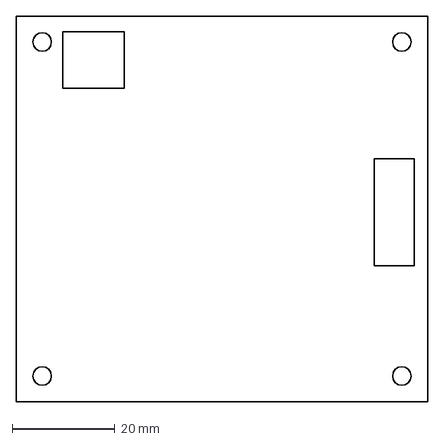
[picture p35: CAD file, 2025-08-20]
3d_models/shield_cmod/model.dxf
80.0 x 75.0 mm

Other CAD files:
3d_models/large_spacer/design.f3d
3d_models/motor_enclosure/design.f3d
3d_models/platform/design.f3d
3d_models/r_mech/design.f3d
3d_models/sensor_head/design.f3d
3d_models/shield_cmod/design.f3d

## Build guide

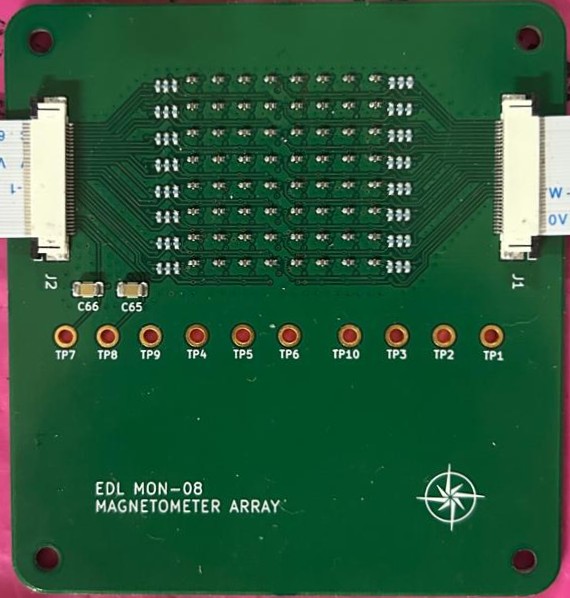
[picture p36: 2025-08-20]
pcb/PCB_1/pictures/EDL_3001_PCB_Front_Assembled.jpeg

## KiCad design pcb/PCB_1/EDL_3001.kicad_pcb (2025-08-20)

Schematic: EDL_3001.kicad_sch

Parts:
C1, C2, C3, C4, C5, C6, C7, C8, C9, C10, C11, C12, C13, C14, C15, C16, C17, C18, C19, C20, C21, C22, C23, C24, C25, C26, C27, C28, C29, C30, C31, C32, C33, C34, C35, C36, C37, C38, C39, C40, C41, C42, C43, C44, C45, C46, C47, C48, C49, C50, C51, C52, C53, C54, C55, C56, C57, C58, C59, C60, C61, C62, C63, C64: 0.1 u; C_0402_1005Metric
C65, C66: 1 u; C_1206_3216Metric
J1, J2: 524353071; 52435-3071
R1, R2, R3, R4, R5, R6, R7, R8, R9, R10, R11, R12, R13, R14, R15, R16, R17, R18, R19, R20, R21, R22, R23, R24, R25, R26, R27, R28, R29, R30, R31, R32, R33, R34, R35, R36, R37, R38, R39, R40, R41, R42, R43, R44, R45, R46, R47, R48: 1.8k; R_0402_1005Metric
TP1, TP2, TP3, TP4, TP5, TP6, TP7, TP8, TP9, TP10: TestPoint; TestPoint_Plated_Hole_D2.0mm
U1, U2, U3, U4, U5, U6, U7, U8, U9, U10, U11, U12, U13, U14, U15, U16, U17, U18, U19, U20, U21, U22, U23, U24, U25, U26, U27, U28, U29, U30, U31, U32, U33, U34, U35, U36, U37, U38, U39, U40, U41, U42, U43, U44, U45, U46, U47, U48, U49, U50, U51, U52, U53, U54, U55, U56, U57, U58, U59, U60, U61, U62, U63, U64: TMAG3001A2YBGR; DSBGA6_YBG_TEX

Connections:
GND: C1.2, C2.2, C3.2, C4.2, C5.2, C6.2, C7.2, C8.2, C9.2, C10.2, C11.2, C12.2, C13.2, C14.2, C15.2, C16.2, C17.2, C18.2, C19.2, C20.2, C21.2, C22.2, C23.2, C24.2, C25.2, C26.2, C27.2, C28.2, C29.2, C30.2, C31.2, C32.2, C33.2, C34.2, C35.2, C36.2, C37.2, C38.2, C39.2, C40.2, C41.2, C42.2, C43.2, C44.2, C45.2, C46.2, C47.2, C48.2, C49.2, C50.2, C51.2, C52.2, C53.2, C54.2, C55.2, C56.2, C57.2, C58.2, C59.2, C60.2, C61.2, C62.2, C63.2, C64.2, C65.2, C66.2, J1.1, J1.2, J1.3, J1.4, J1.5, J1.6, J1.7, J1.8, J1.9, J1.10, J1.31, J1.32, J2.21, J2.22, J2.23, J2.24, J2.25, J2.27, J2.29, J2.30, J2.31, J2.32, TP9.1, TP10.1, U1.B2 (GND), U2.A2 (ADDR), U2.B2 (GND), U3.B2 (GND), U4.B2 (GND), U5.B2 (GND), U6.A2 (ADDR), U6.B2 (GND), U7.B2 (GND), U8.B2 (GND), U9.B2 (GND), U10.A2 (ADDR), U10.B2 (GND), U11.B2 (GND), U12.B2 (GND), U13.B2 (GND), U14.A2 (ADDR), U14.B2 (GND), U15.B2 (GND), U16.B2 (GND), U17.B2 (GND), U18.A2 (ADDR), U18.B2 (GND), U19.B2 (GND), U20.B2 (GND), U21.B2 (GND), U22.A2 (ADDR), U22.B2 (GND), U23.B2 (GND), U24.B2 (GND), U25.B2 (GND), U26.A2 (ADDR), U26.B2 (GND), U27.B2 (GND), U28.B2 (GND), U29.B2 (GND), U30.A2 (ADDR), U30.B2 (GND), U31.B2 (GND), U32.B2 (GND), U33.B2 (GND), U34.A2 (ADDR), U34.B2 (GND), U35.B2 (GND), U36.B2 (GND), U37.B2 (GND), U38.A2 (ADDR), U38.B2 (GND), U39.B2 (GND), U40.B2 (GND), U41.B2 (GND), U42.A2 (ADDR), U42.B2 (GND), U43.B2 (GND), U44.B2 (GND), U45.B2 (GND), U46.A2 (ADDR), U46.B2 (GND), U47.B2 (GND), U48.B2 (GND), U49.B2 (GND), U50.A2 (ADDR), U50.B2 (GND), U51.B2 (GND), U52.B2 (GND), U53.B2 (GND), U54.A2 (ADDR), U54.B2 (GND), U55.B2 (GND), U56.B2 (GND), U57.B2 (GND), U58.A2 (ADDR), U58.B2 (GND), U59.B2 (GND), U60.B2 (GND), U61.B2 (GND), U62.A2 (ADDR), U62.B2 (GND), U63.B2 (GND), U64.B2 (GND)
unnamed: R33.2, R34.1
unnamed: R35.2, R36.1
unnamed: R37.2, R38.1
unnamed: R39.2, R40.1
unnamed: R41.2, R42.1
unnamed: R43.2, R44.1
unnamed: R45.2, R46.1
unnamed: R47.2, R48.1
unnamed: J1.30, R34.2, U1.B1 (*INT), U2.B1 (*INT), U3.B1 (*INT), U4.B1 (*INT), U5.B1 (*INT), U6.B1 (*INT), U7.B1 (*INT), U8.B1 (*INT)
unnamed: J1.29, R1.2, U1.C2 (SCL), U2.C2 (SCL), U3.C2 (SCL), U4.A2 (ADDR), U4.C2 (SCL)
unnamed: J1.28, R2.2, U1.C1 (SDA), U2.C1 (SDA), U3.A2 (ADDR), U3.C1 (SDA), U4.C1 (SDA)
unnamed: J1.27, R3.2, U5.C2 (SCL), U6.C2 (SCL), U7.C2 (SCL), U8.A2 (ADDR), U8.C2 (SCL)
unnamed: J1.26, R4.2, U5.C1 (SDA), U6.C1 (SDA), U7.A2 (ADDR), U7.C1 (SDA), U8.C1 (SDA)
unnamed: J1.25, R36.2, U9.B1 (*INT), U10.B1 (*INT), U11.B1 (*INT), U12.B1 (*INT), U13.B1 (*INT), U14.B1 (*INT), U15.B1 (*INT), U16.B1 (*INT)
unnamed: J1.24, R5.2, U9.C2 (SCL), U10.C2 (SCL), U11.C2 (SCL), U12.A2 (ADDR), U12.C2 (SCL)
unnamed: J1.23, R6.2, U9.C1 (SDA), U10.C1 (SDA), U11.A2 (ADDR), U11.C1 (SDA), U12.C1 (SDA)
unnamed: J1.22, R7.2, U13.C2 (SCL), U14.C2 (SCL), U15.C2 (SCL), U16.A2 (ADDR), U16.C2 (SCL)
unnamed: J1.21, R8.2, U13.C1 (SDA), U14.C1 (SDA), U15.A2 (ADDR), U15.C1 (SDA), U16.C1 (SDA)
unnamed: J1.20, R38.2, U17.B1 (*INT), U18.B1 (*INT), U19.B1 (*INT), U20.B1 (*INT), U21.B1 (*INT), U22.B1 (*INT), U23.B1 (*INT), U24.B1 (*INT)
unnamed: J1.19, R9.2, U17.C2 (SCL), U18.C2 (SCL), U19.C2 (SCL), U20.A2 (ADDR), U20.C2 (SCL)
unnamed: J1.18, R10.2, U17.C1 (SDA), U18.C1 (SDA), U19.A2 (ADDR), U19.C1 (SDA), U20.C1 (SDA)
unnamed: J1.17, R11.2, U21.C2 (SCL), U22.C2 (SCL), U23.C2 (SCL), U24.A2 (ADDR), U24.C2 (SCL)
unnamed: J1.16, R12.2, U21.C1 (SDA), U22.C1 (SDA), U23.A2 (ADDR), U23.C1 (SDA), U24.C1 (SDA)
unnamed: J1.15, R40.2, TP1.1, U25.B1 (*INT), U26.B1 (*INT), U27.B1 (*INT), U28.B1 (*INT), U29.B1 (*INT), U30.B1 (*INT), U31.B1 (*INT), U32.B1 (*INT)
unnamed: J1.14, R13.2, U25.C2 (SCL), U26.C2 (SCL), U27.C2 (SCL), U28.A2 (ADDR), U28.C2 (SCL)
unnamed: J1.13, R14.2, U25.C1 (SDA), U26.C1 (SDA), U27.A2 (ADDR), U27.C1 (SDA), U28.C1 (SDA)
unnamed: J1.12, R15.2, TP2.1, U29.C2 (SCL), U30.C2 (SCL), U31.C2 (SCL), U32.A2 (ADDR), U32.C2 (SCL)
unnamed: J1.11, R16.2, TP3.1, U29.C1 (SDA), U30.C1 (SDA), U31.A2 (ADDR), U31.C1 (SDA), U32.C1 (SDA)
unnamed: J2.1, R42.2, U33.B1 (*INT), U34.B1 (*INT), U35.B1 (*INT), U36.B1 (*INT), U37.B1 (*INT), U38.B1 (*INT), U39.B1 (*INT), U40.B1 (*INT)
unnamed: J2.2, R17.2, U33.C2 (SCL), U34.C2 (SCL), U35.C2 (SCL), U36.A2 (ADDR), U36.C2 (SCL)
unnamed: J2.3, R18.2, U33.C1 (SDA), U34.C1 (SDA), U35.A2 (ADDR), U35.C1 (SDA), U36.C1 (SDA)
unnamed: J2.4, R19.2, U37.C2 (SCL), U38.C2 (SCL), U39.C2 (SCL), U40.A2 (ADDR), U40.C2 (SCL)
unnamed: J2.5, R20.2, U37.C1 (SDA), U38.C1 (SDA), U39.A2 (ADDR), U39.C1 (SDA), U40.C1 (SDA)
unnamed: J2.6, R44.2, U41.B1 (*INT), U42.B1 (*INT), U43.B1 (*INT), U44.B1 (*INT), U45.B1 (*INT), U46.B1 (*INT), U47.B1 (*INT), U48.B1 (*INT)
unnamed: J2.7, R21.2, U41.C2 (SCL), U42.C2 (SCL), U43.C2 (SCL), U44.A2 (ADDR), U44.C2 (SCL)
unnamed: J2.8, R22.2, U41.C1 (SDA), U42.C1 (SDA), U43.A2 (ADDR), U43.C1 (SDA), U44.C1 (SDA)
unnamed: J2.9, R23.2, U45.C2 (SCL), U46.C2 (SCL), U47.C2 (SCL), U48.A2 (ADDR), U48.C2 (SCL)
unnamed: J2.10, R24.2, U45.C1 (SDA), U46.C1 (SDA), U47.A2 (ADDR), U47.C1 (SDA), U48.C1 (SDA)
unnamed: J2.11, R46.2, U49.B1 (*INT), U50.B1 (*INT), U51.B1 (*INT), U52.B1 (*INT), U53.B1 (*INT), U54.B1 (*INT), U55.B1 (*INT), U56.B1 (*INT)
unnamed: J2.12, R25.2, U49.C2 (SCL), U50.C2 (SCL), U51.C2 (SCL), U52.A2 (ADDR), U52.C2 (SCL)
unnamed: J2.13, R26.2, U49.C1 (SDA), U50.C1 (SDA), U51.A2 (ADDR), U51.C1 (SDA), U52.C1 (SDA)
unnamed: J2.14, R27.2, U53.C2 (SCL), U54.C2 (SCL), U55.C2 (SCL), U56.A2 (ADDR), U56.C2 (SCL)
unnamed: J2.15, R28.2, U53.C1 (SDA), U54.C1 (SDA), U55.A2 (ADDR), U55.C1 (SDA), U56.C1 (SDA)
unnamed: J2.16, R48.2, TP4.1, U57.B1 (*INT), U58.B1 (*INT), U59.B1 (*INT), U60.B1 (*INT), U61.B1 (*INT), U62.B1 (*INT), U63.B1 (*INT), U64.B1 (*INT)
unnamed: J2.17, R29.2, U57.C2 (SCL), U58.C2 (SCL), U59.C2 (SCL), U60.A2 (ADDR), U60.C2 (SCL)
unnamed: J2.18, R30.2, U57.C1 (SDA), U58.C1 (SDA), U59.A2 (ADDR), U59.C1 (SDA), U60.C1 (SDA)
unnamed: J2.19, R31.2, TP5.1, U61.C2 (SCL), U62.C2 (SCL), U63.C2 (SCL), U64.A2 (ADDR), U64.C2 (SCL)
unnamed: J2.20, R32.2, TP6.1, U61.C1 (SDA), U62.C1 (SDA), U63.A2 (ADDR), U63.C1 (SDA), U64.C1 (SDA)
VCC: C1.1, C2.1, C3.1, C4.1, C5.1, C6.1, C7.1, C8.1, C9.1, C10.1, C11.1, C12.1, C13.1, C14.1, C15.1, C16.1, C17.1, C18.1, C19.1, C20.1, C21.1, C22.1, C23.1, C24.1, C25.1, C26.1, C27.1, C28.1, C29.1, C30.1, C31.1, C32.1, C66.1, J2.28, R1.1, R2.1, R3.1, R4.1, R5.1, R6.1, R7.1, R8.1, R9.1, R10.1, R11.1, R12.1, R13.1, R14.1, R15.1, R16.1, R33.1, R35.1, R37.1, R39.1, TP7.1, U1.A1 (VCC), U1.A2 (ADDR), U2.A1 (VCC), U3.A1 (VCC), U4.A1 (VCC), U5.A1 (VCC), U5.A2 (ADDR), U6.A1 (VCC), U7.A1 (VCC), U8.A1 (VCC), U9.A1 (VCC), U9.A2 (ADDR), U10.A1 (VCC), U11.A1 (VCC), U12.A1 (VCC), U13.A1 (VCC), U13.A2 (ADDR), U14.A1 (VCC), U15.A1 (VCC), U16.A1 (VCC), U17.A1 (VCC), U17.A2 (ADDR), U18.A1 (VCC), U19.A1 (VCC), U20.A1 (VCC), U21.A1 (VCC), U21.A2 (ADDR), U22.A1 (VCC), U23.A1 (VCC), U24.A1 (VCC), U25.A1 (VCC), U25.A2 (ADDR), U26.A1 (VCC), U27.A1 (VCC), U28.A1 (VCC), U29.A1 (VCC), U29.A2 (ADDR), U30.A1 (VCC), U31.A1 (VCC), U32.A1 (VCC)
VCC2: C33.1, C34.1, C35.1, C36.1, C37.1, C38.1, C39.1, C40.1, C41.1, C42.1, C43.1, C44.1, C45.1, C46.1, C47.1, C48.1, C49.1, C50.1, C51.1, C52.1, C53.1, C54.1, C55.1, C56.1, C57.1, C58.1, C59.1, C60.1, C61.1, C62.1, C63.1, C64.1, C65.1, J2.26, R17.1, R18.1, R19.1, R20.1, R21.1, R22.1, R23.1, R24.1, R25.1, R26.1, R27.1, R28.1, R29.1, R30.1, R31.1, R32.1, R41.1, R43.1, R45.1, R47.1, TP8.1, U33.A1 (VCC), U33.A2 (ADDR), U34.A1 (VCC), U35.A1 (VCC), U36.A1 (VCC), U37.A1 (VCC), U37.A2 (ADDR), U38.A1 (VCC), U39.A1 (VCC), U40.A1 (VCC), U41.A1 (VCC), U41.A2 (ADDR), U42.A1 (VCC), U43.A1 (VCC), U44.A1 (VCC), U45.A1 (VCC), U45.A2 (ADDR), U46.A1 (VCC), U47.A1 (VCC), U48.A1 (VCC), U49.A1 (VCC), U49.A2 (ADDR), U50.A1 (VCC), U51.A1 (VCC), U52.A1 (VCC), U53.A1 (VCC), U53.A2 (ADDR), U54.A1 (VCC), U55.A1 (VCC), U56.A1 (VCC), U57.A1 (VCC), U57.A2 (ADDR), U58.A1 (VCC), U59.A1 (VCC), U60.A1 (VCC), U61.A1 (VCC), U61.A2 (ADDR), U62.A1 (VCC), U63.A1 (VCC), U64.A1 (VCC)

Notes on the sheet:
MAGNETOMETER ARRAY (8X8)
Power Supply

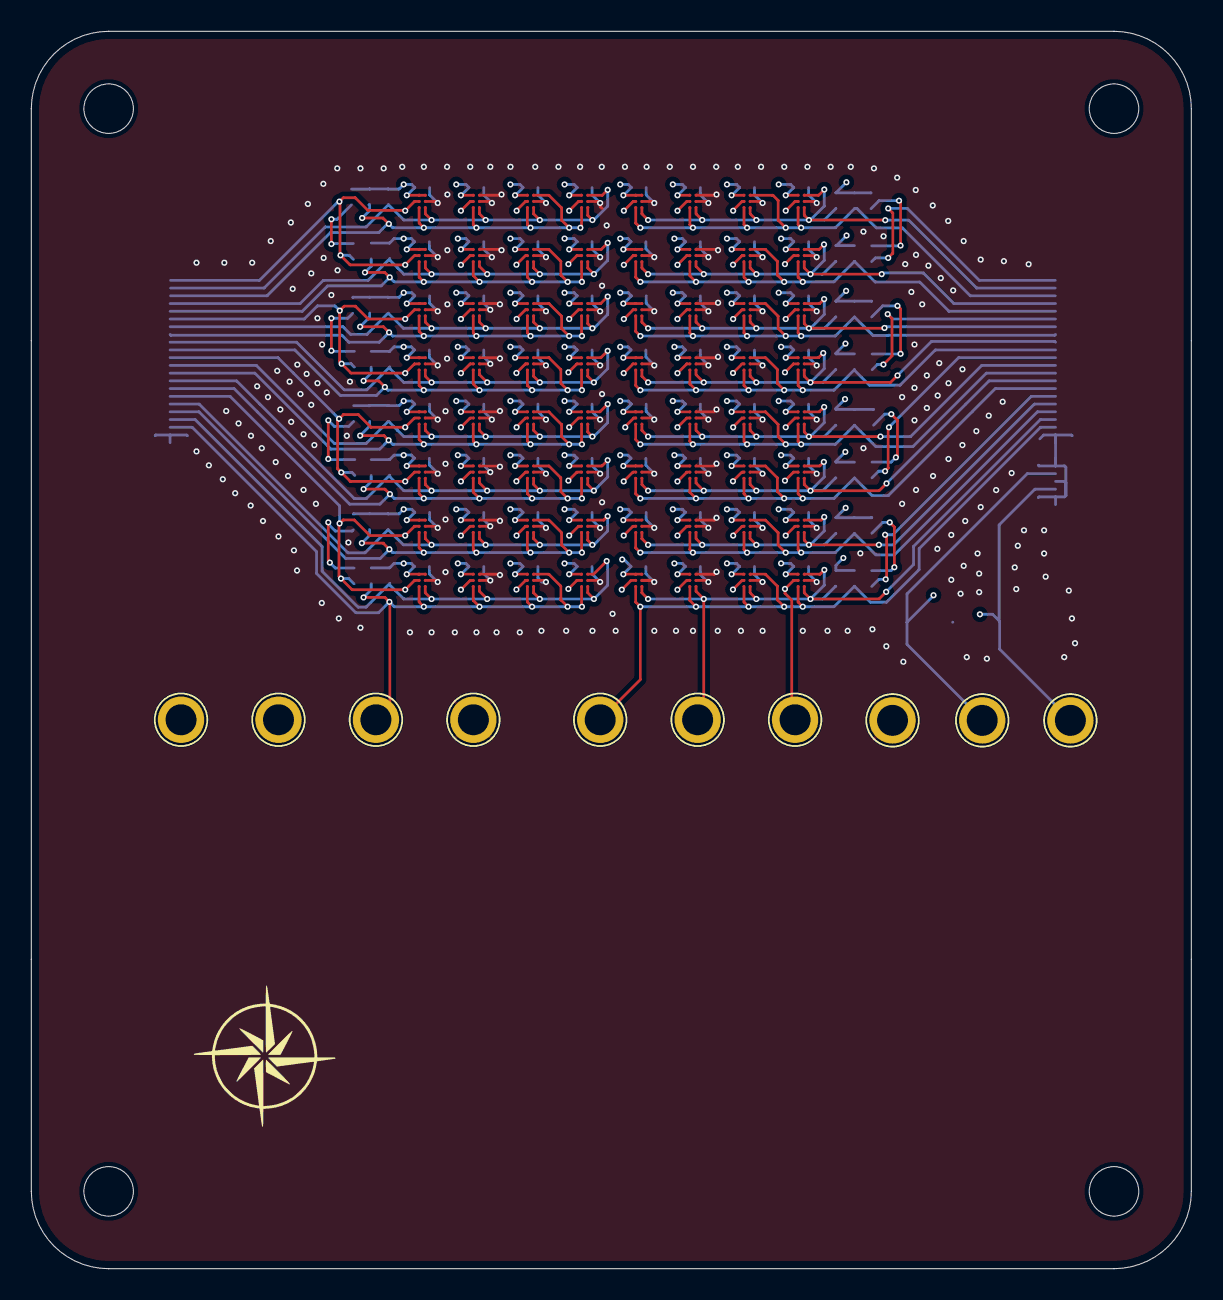
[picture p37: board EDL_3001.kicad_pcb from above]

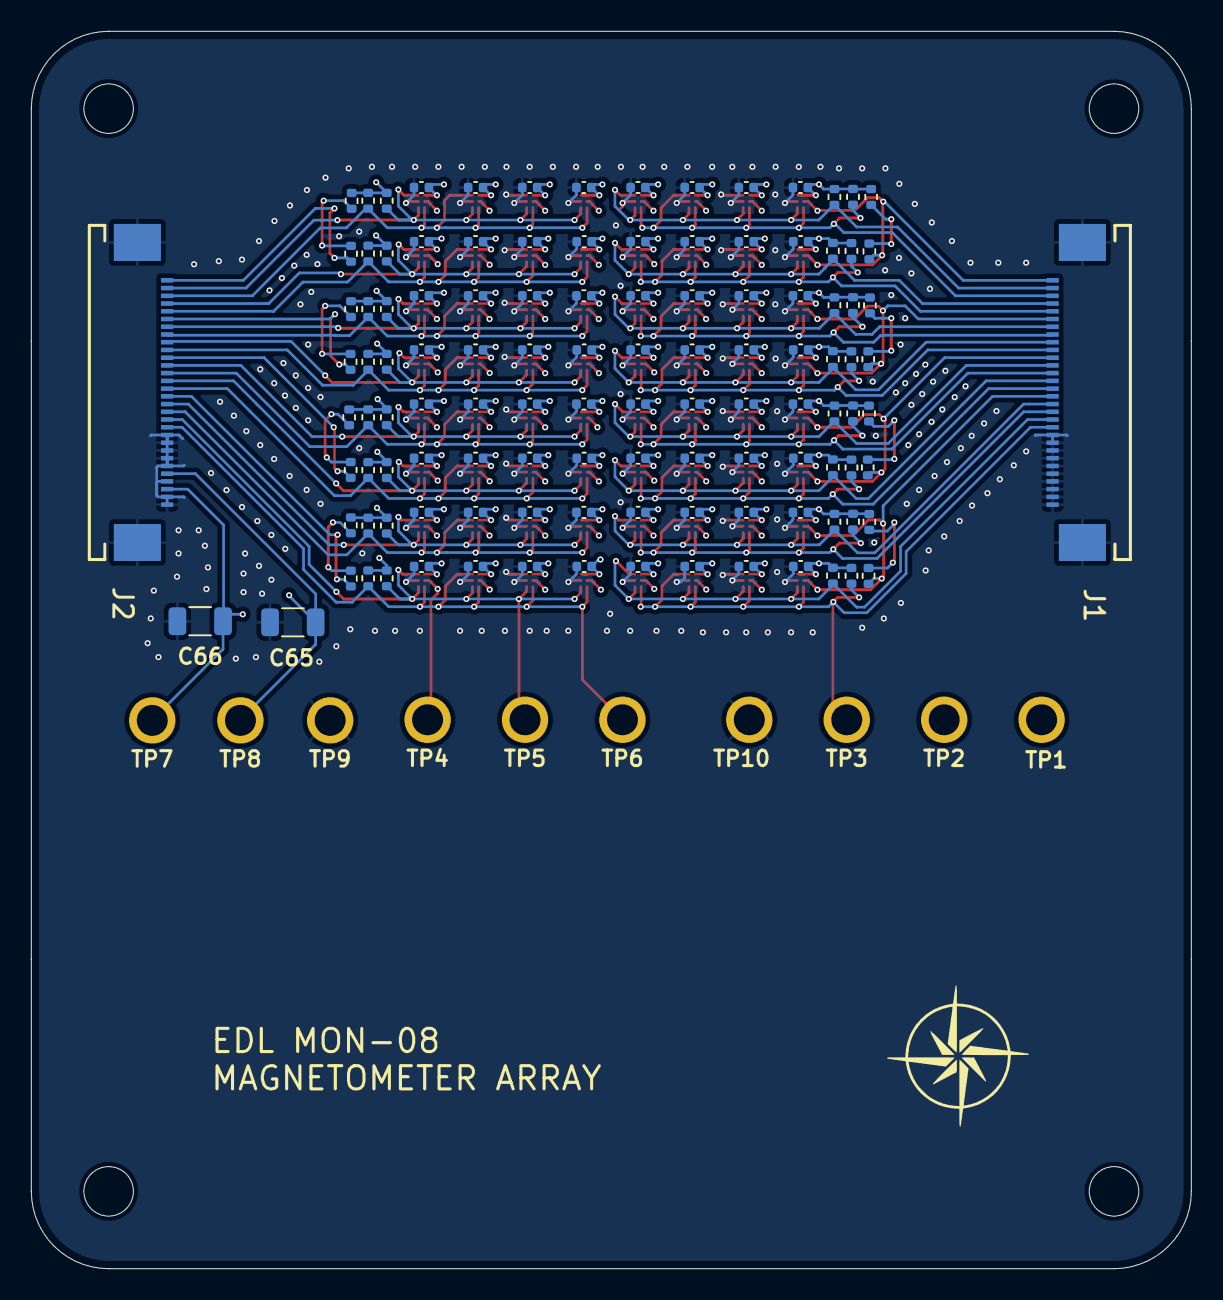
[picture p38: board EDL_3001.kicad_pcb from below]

Board: 4 copper layers, 75.0 x 80.0 mm, 190 parts (116 on the bottom side), 51 nets.

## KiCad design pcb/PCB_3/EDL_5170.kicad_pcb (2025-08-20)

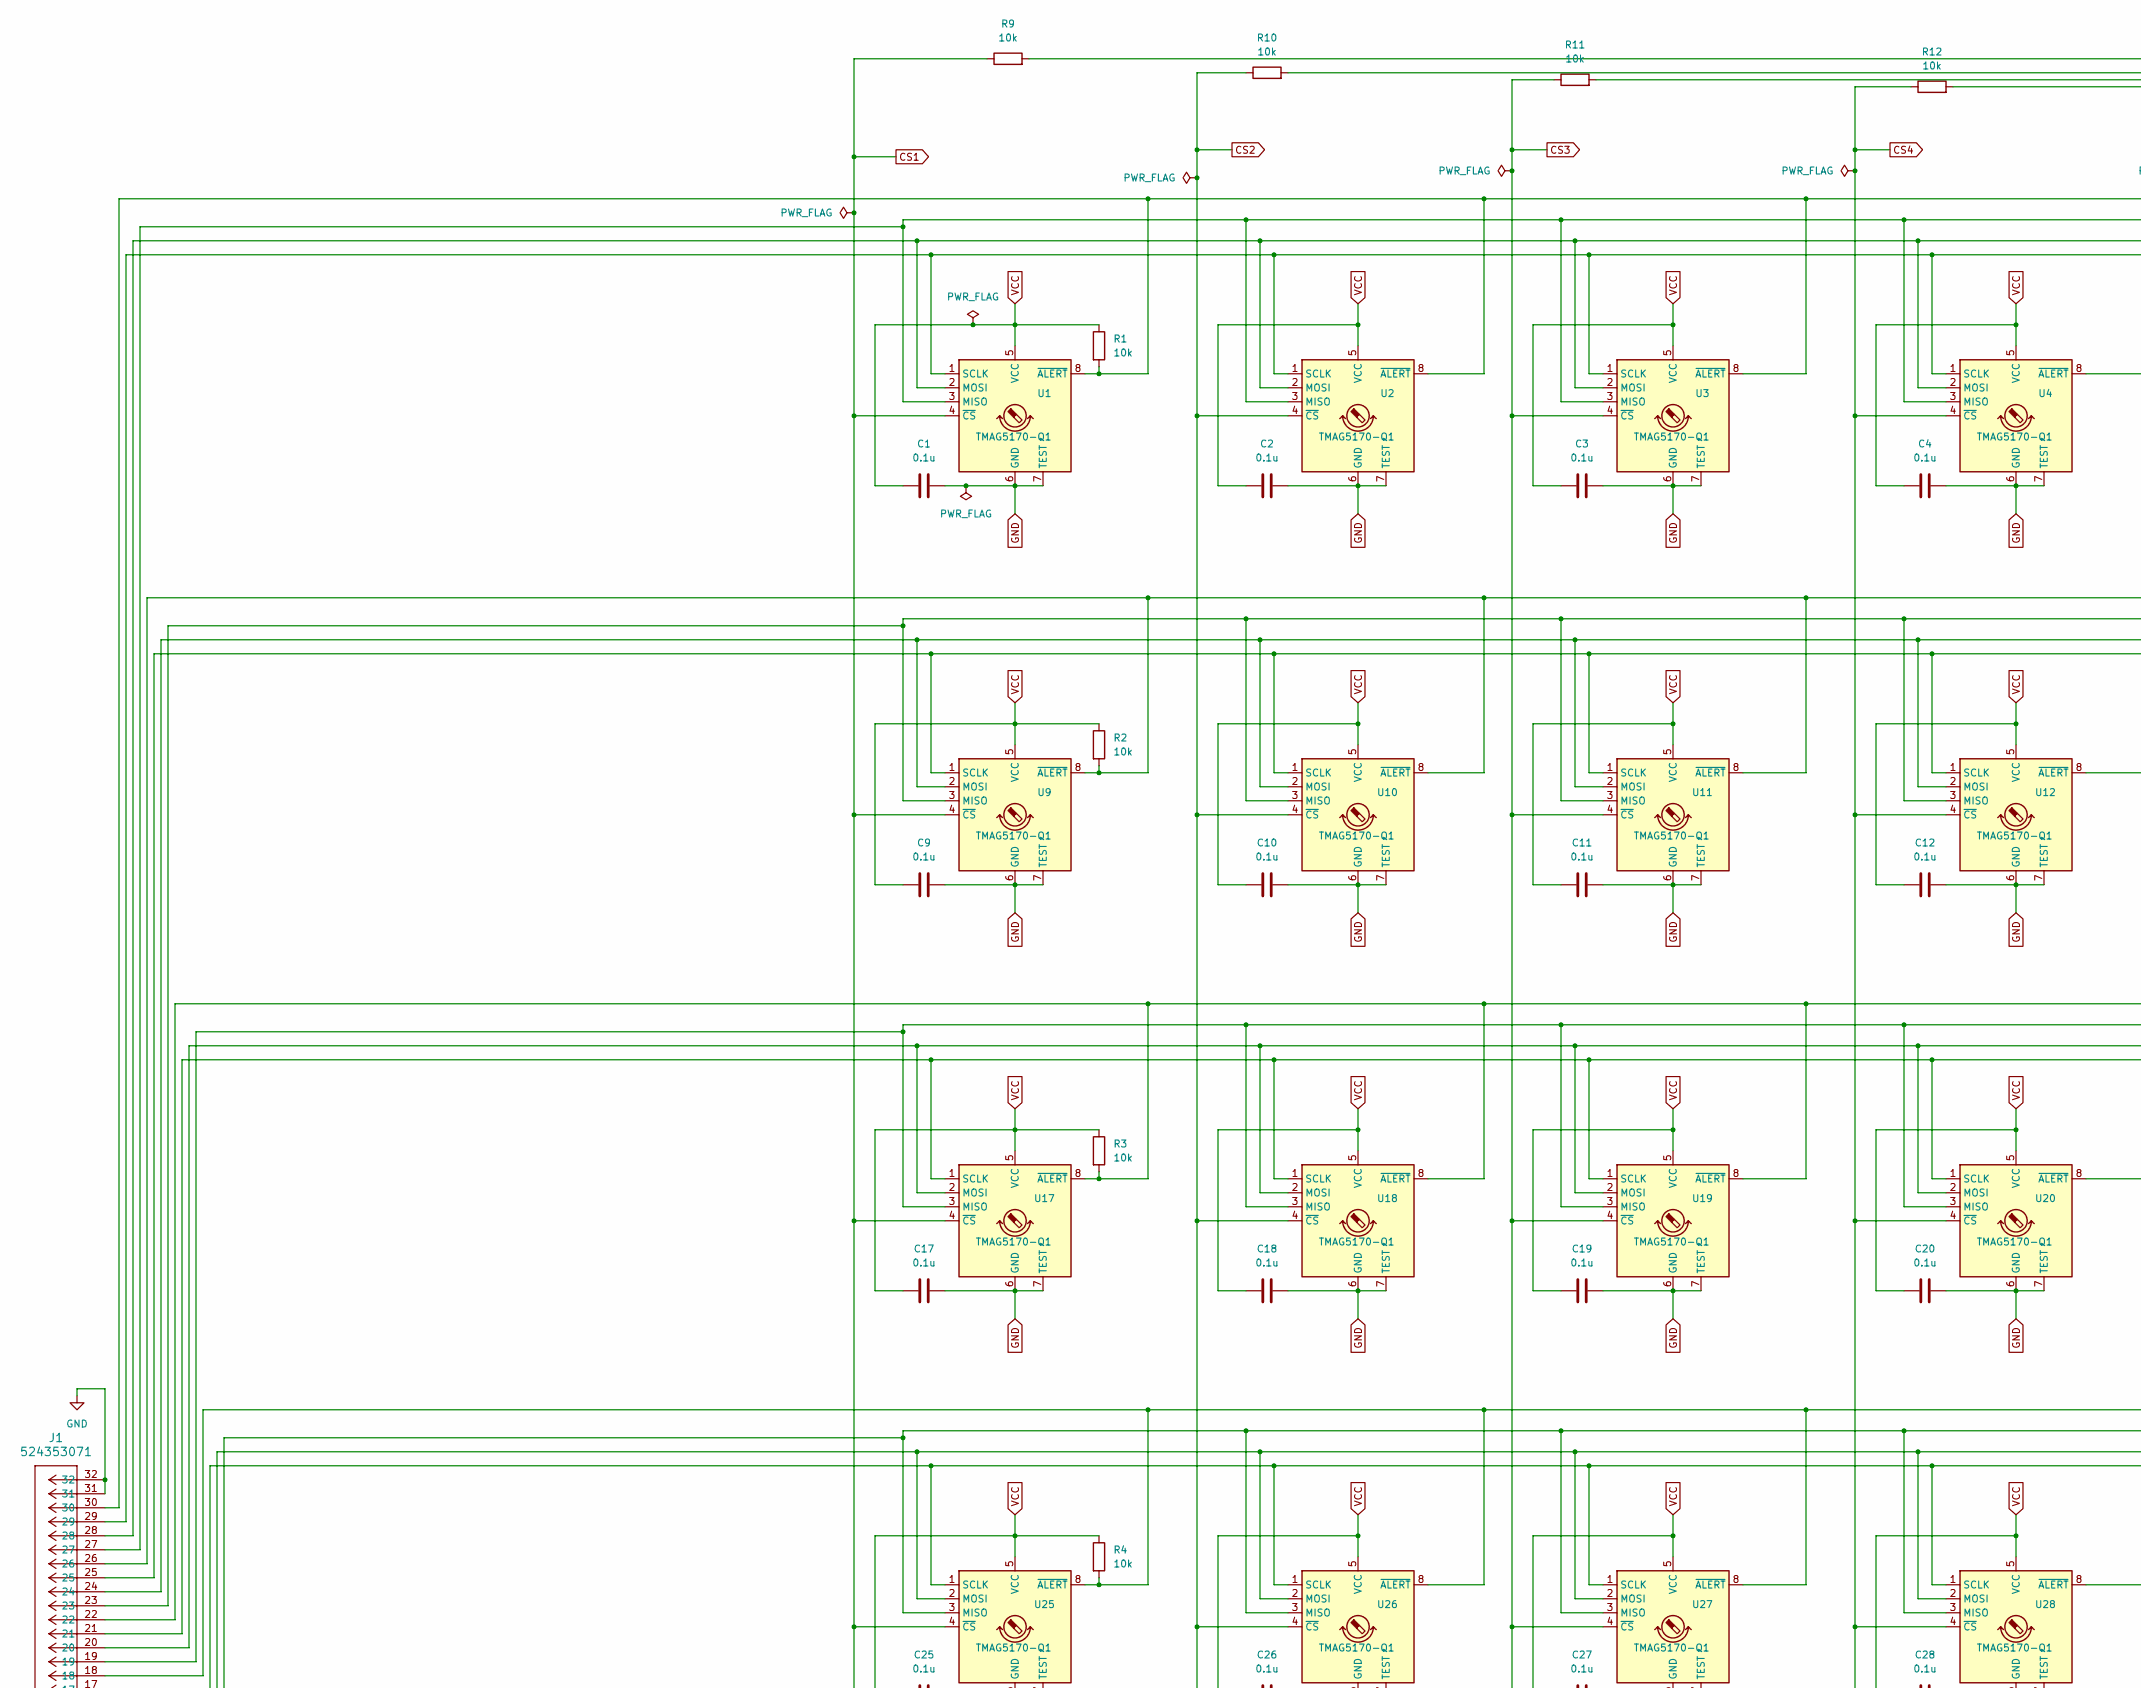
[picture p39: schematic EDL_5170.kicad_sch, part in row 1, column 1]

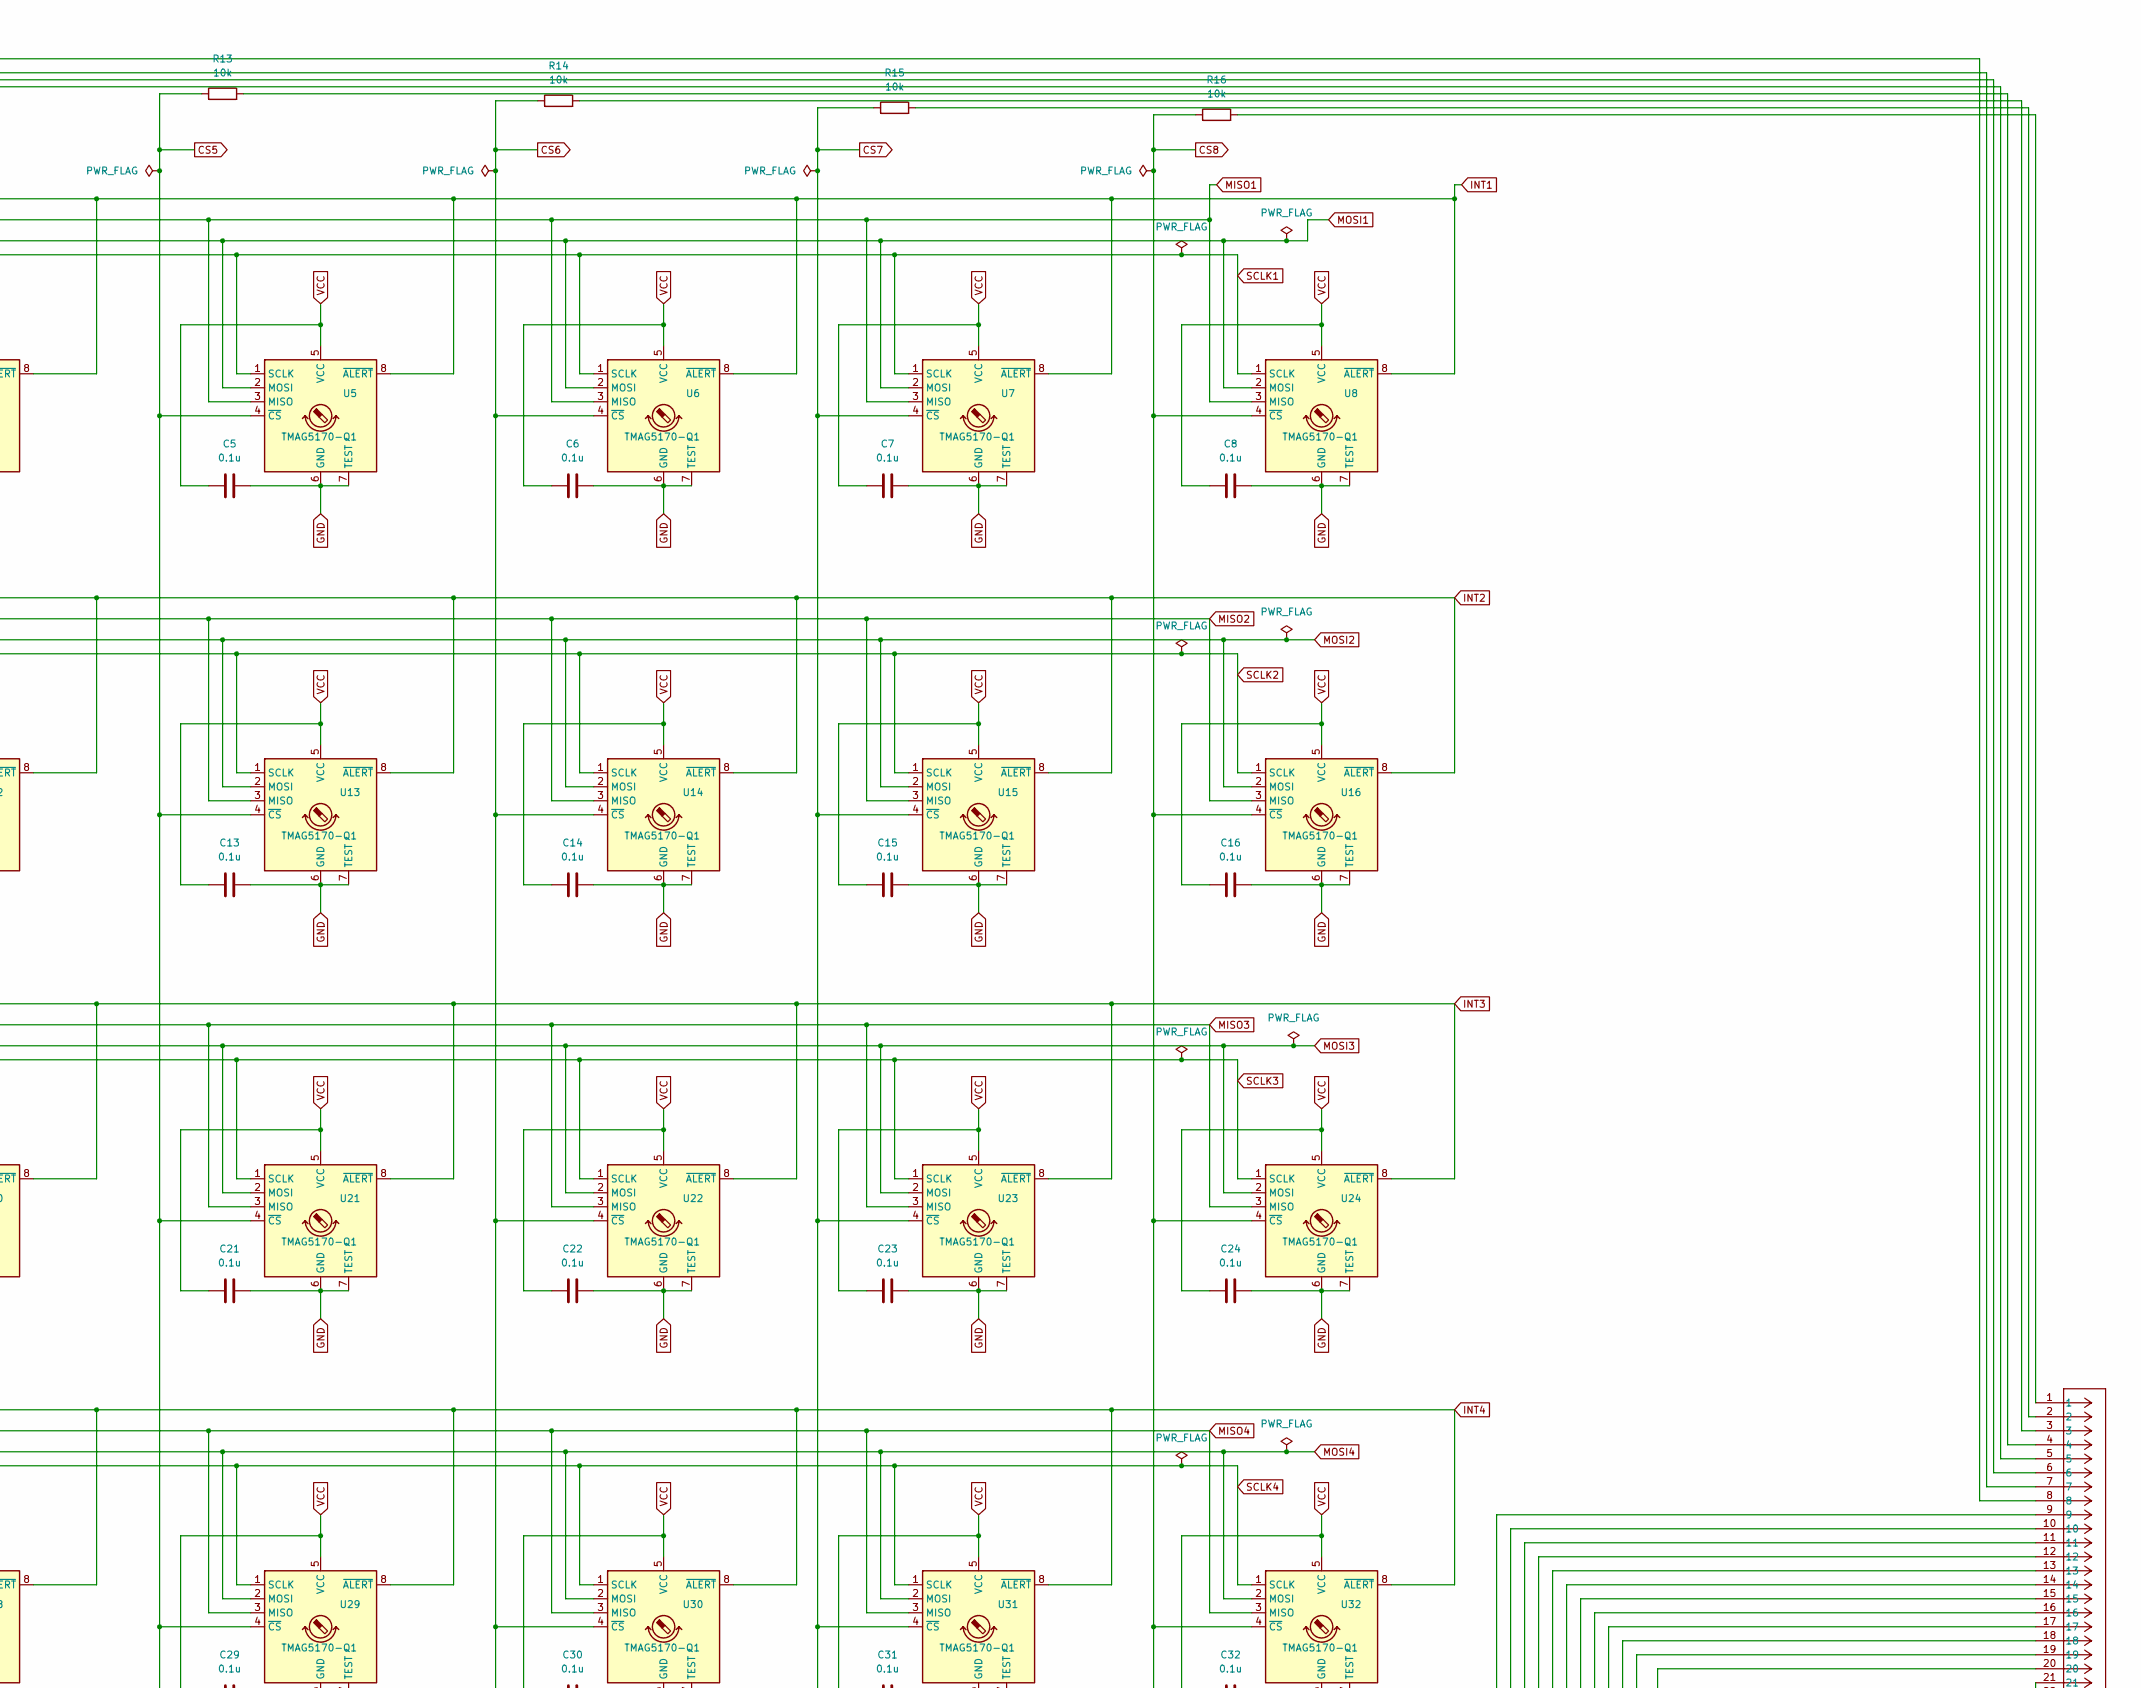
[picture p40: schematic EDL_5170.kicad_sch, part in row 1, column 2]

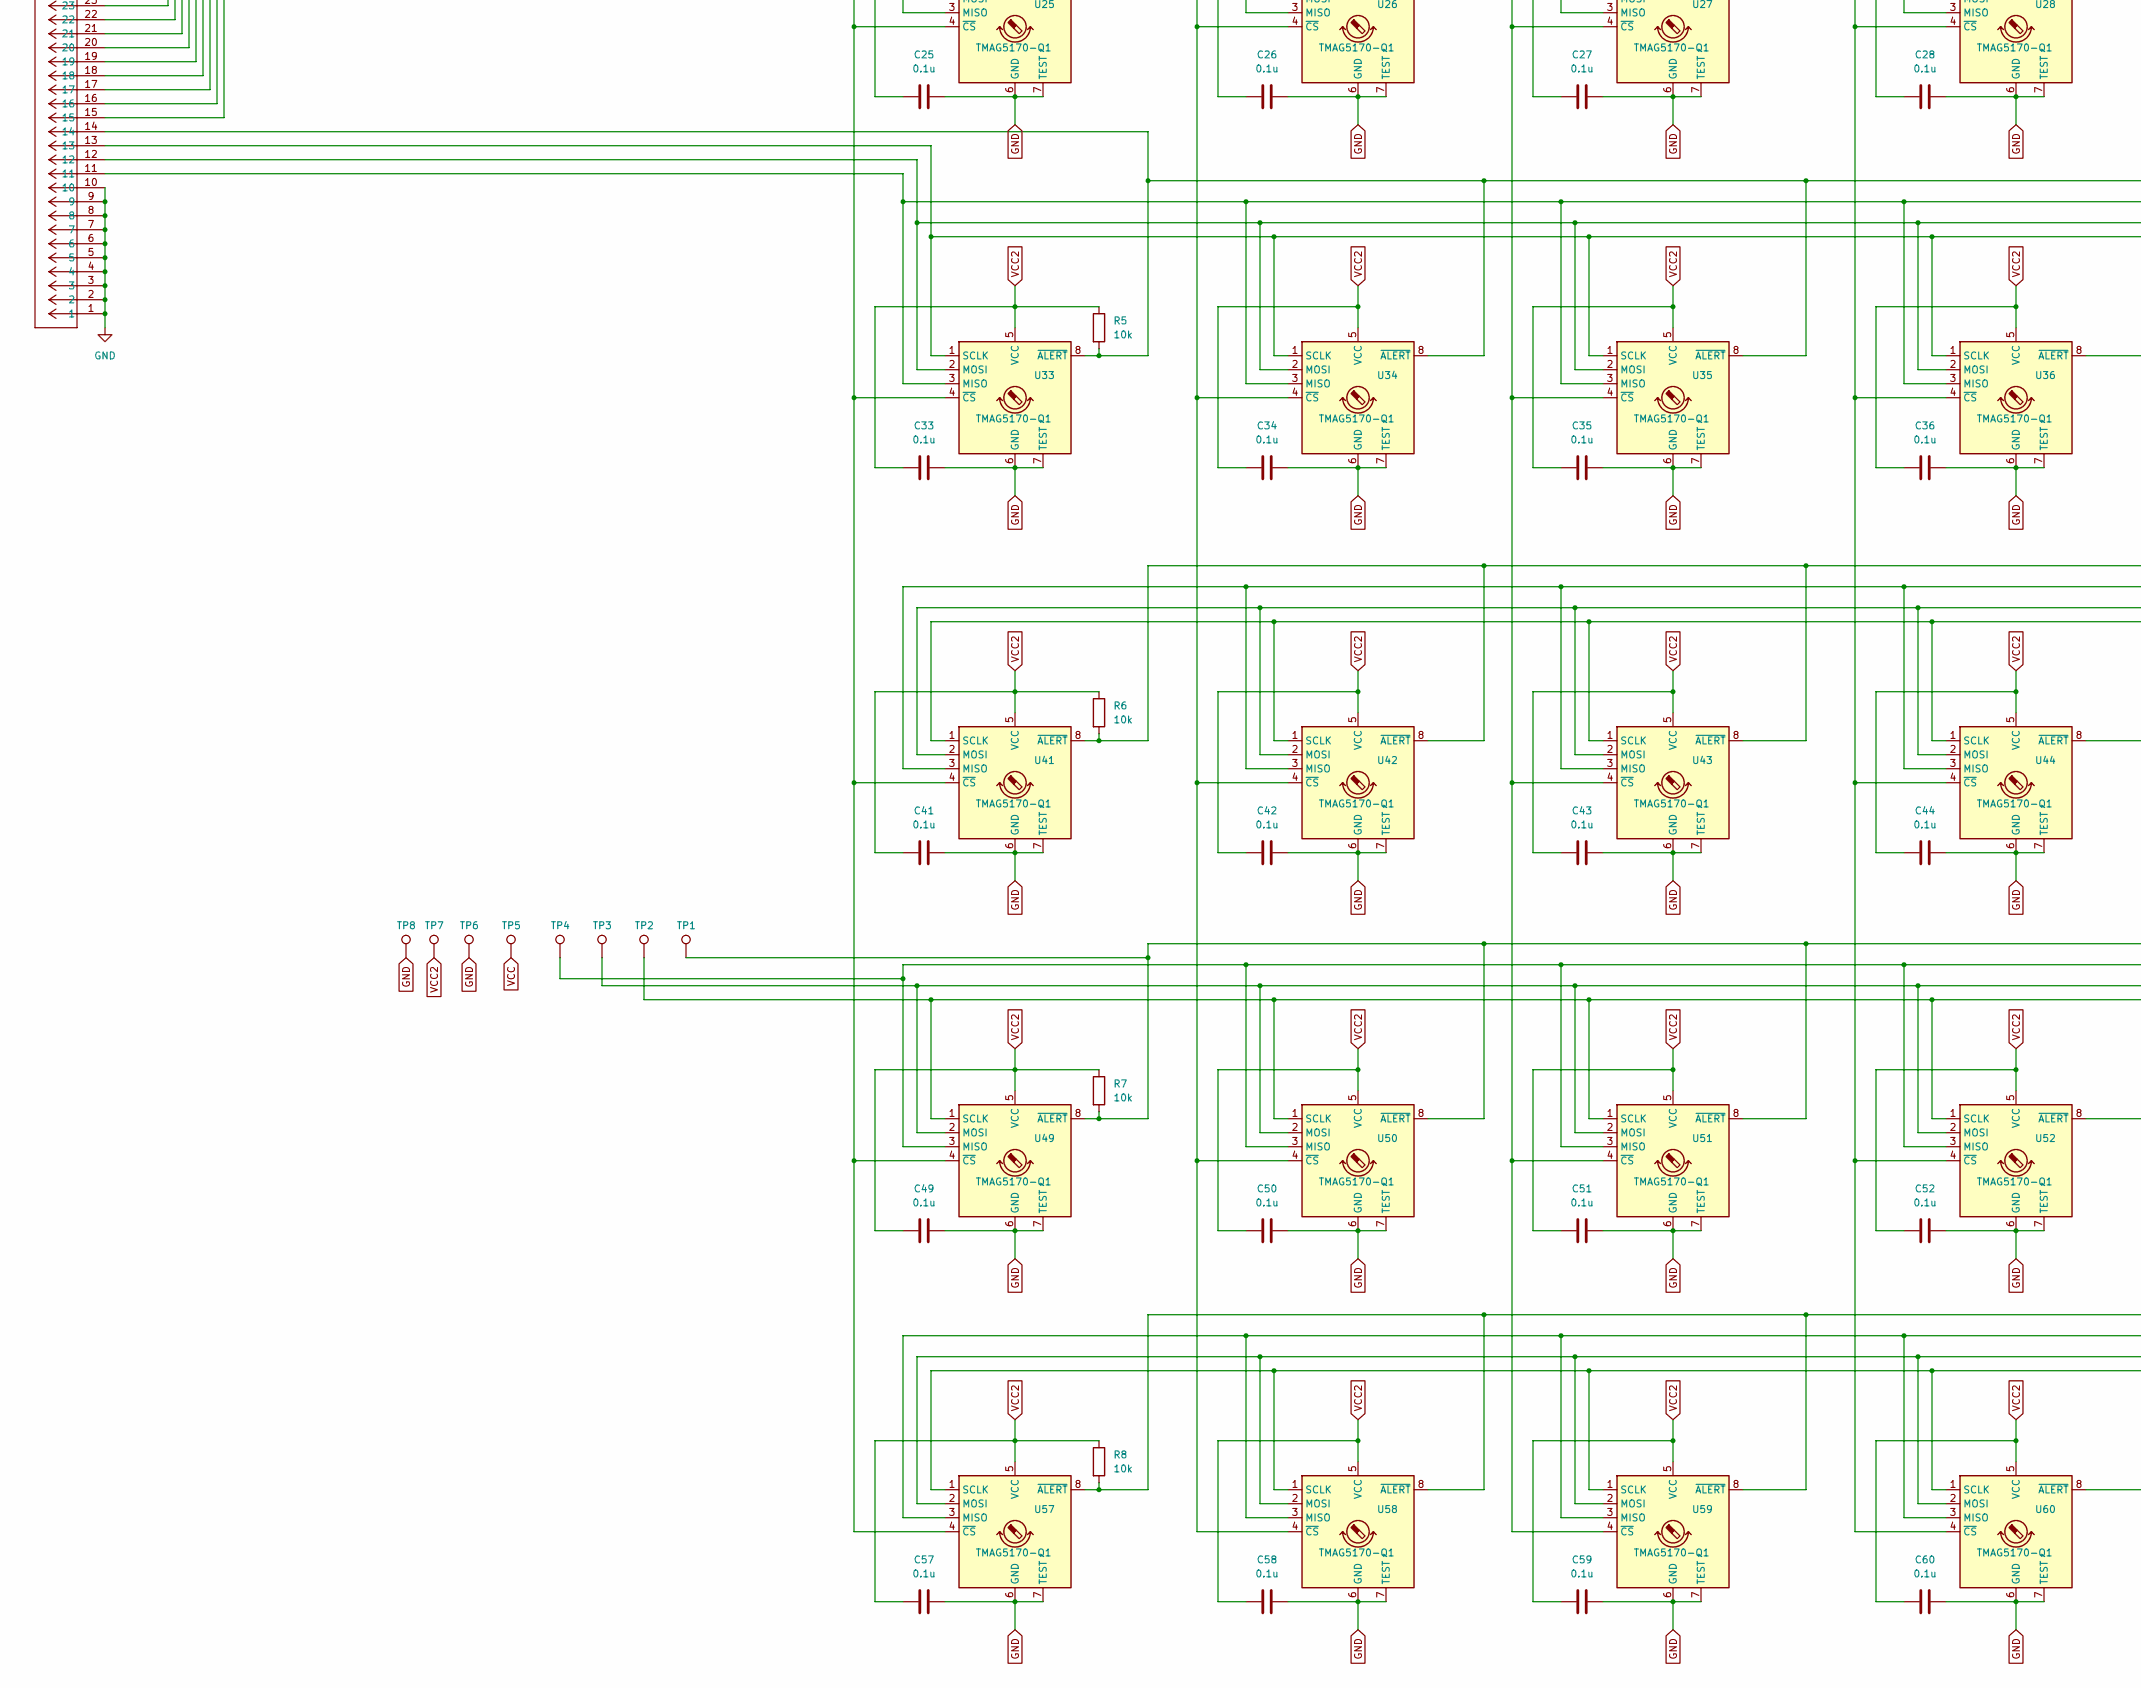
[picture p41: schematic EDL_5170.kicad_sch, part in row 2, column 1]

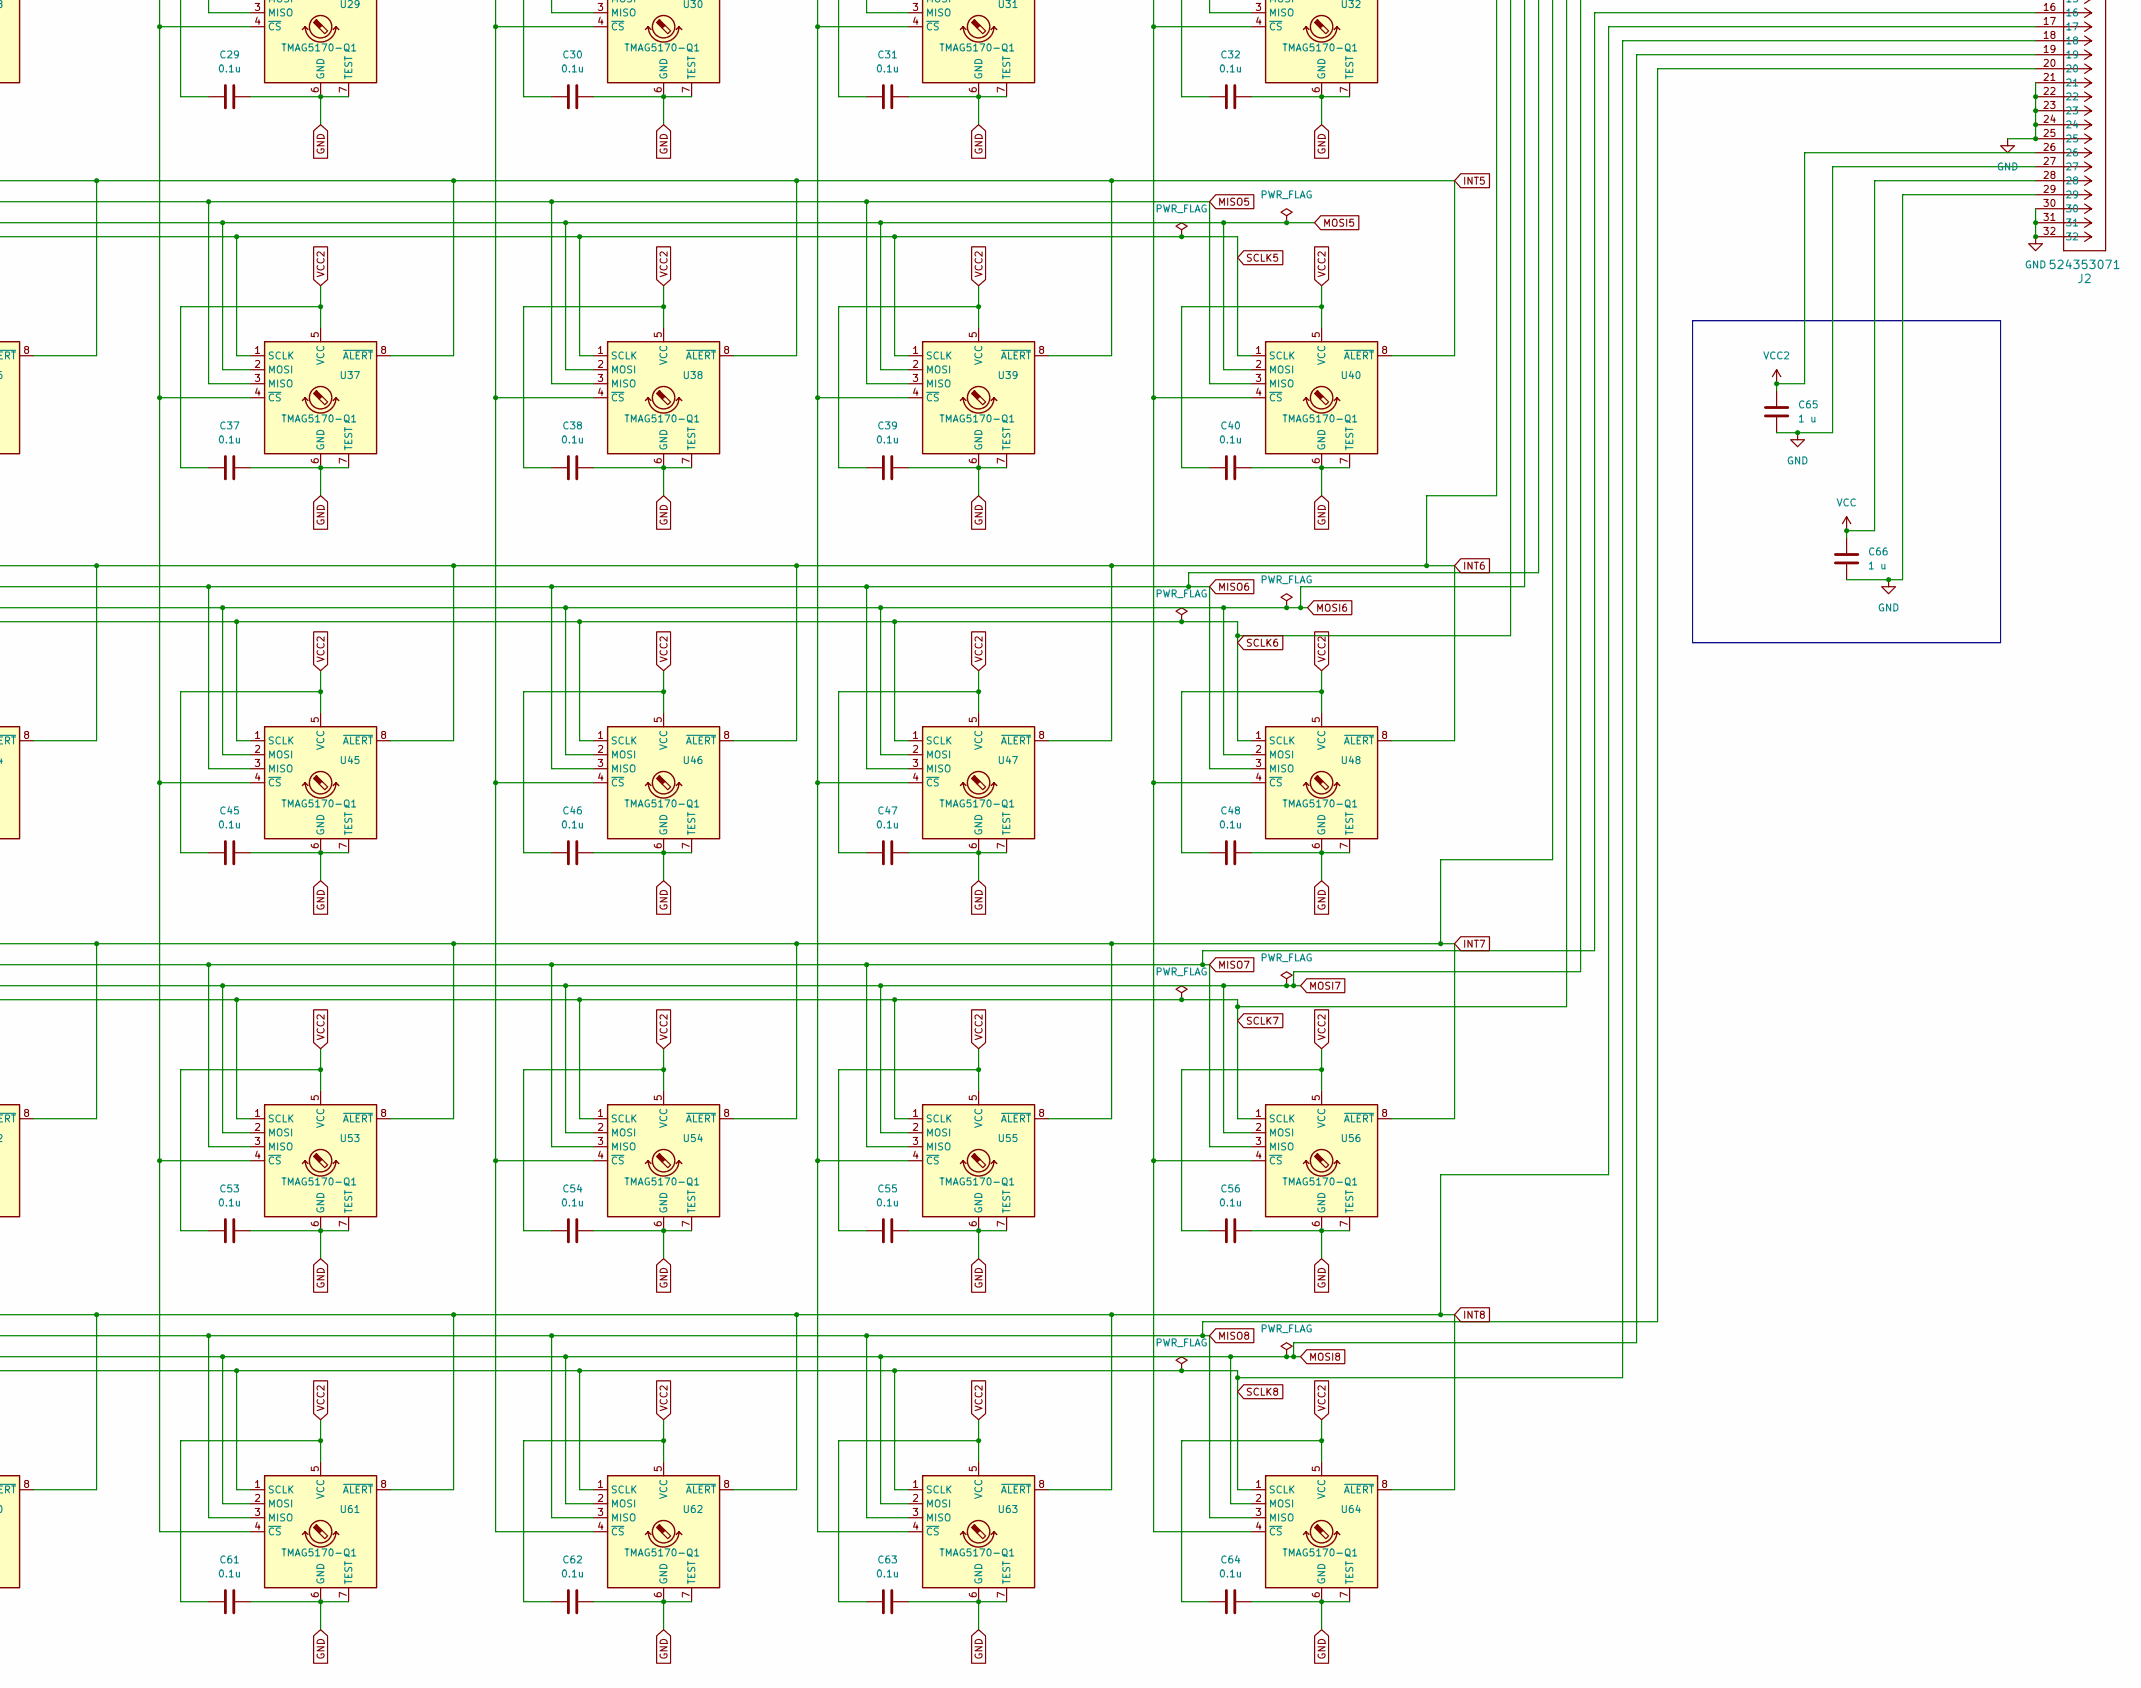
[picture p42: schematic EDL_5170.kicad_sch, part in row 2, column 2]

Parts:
C1, C2, C3, C4, C5, C6, C7, C8, C9, C10, C11, C12, C13, C14, C15, C16, C17, C18, C19, C20, C21, C22, C23, C24, C25, C26, C27, C28, C29, C30, C31, C32, C33, C34, C35, C36, C37, C38, C39, C40, C41, C42, C43, C44, C45, C46, C47, C48, C49, C50, C51, C52, C53, C54, C55, C56, C57, C58, C59, C60, C61, C62, C63, C64: 0.1u; C_1206_3216Metric_Pad1.33x1.80mm_HandSolder
C65, C66: 1 u; C_1206_3216Metric
J1, J2: 524353071; 52435-3071
R1, R2, R3, R4, R5, R6, R7, R8, R9, R10, R11, R12, R13, R14, R15, R16: 10k; R_1206_3216Metric_Pad1.30x1.75mm_HandSolder
TP1, TP2, TP3, TP4, TP5, TP6, TP7, TP8: TestPoint; TestPoint_Plated_Hole_D2.0mm
U1, U2, U3, U4, U5, U6, U7, U8, U9, U10, U11, U12, U13, U14, U15, U16, U17, U18, U19, U20, U21, U22, U23, U24, U25, U26, U27, U28, U29, U30, U31, U32, U33, U34, U35, U36, U37, U38, U39, U40, U41, U42, U43, U44, U45, U46, U47, U48, U49, U50, U51, U52, U53, U54, U55, U56, U57, U58, U59, U60, U61, U62, U63, U64: TMAG5170-Q1; Texas_S-PDSO-G8_3x3mm_P0.65mm

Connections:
CS1: R9.1, U1.4 (~CS), U9.4 (~CS), U17.4 (~CS), U25.4 (~CS), U33.4 (~CS), U41.4 (~CS), U49.4 (~CS), U57.4 (~CS)
CS2: R10.1, U2.4 (~CS), U10.4 (~CS), U18.4 (~CS), U26.4 (~CS), U34.4 (~CS), U42.4 (~CS), U50.4 (~CS), U58.4 (~CS)
CS3: R11.1, U3.4 (~CS), U11.4 (~CS), U19.4 (~CS), U27.4 (~CS), U35.4 (~CS), U43.4 (~CS), U51.4 (~CS), U59.4 (~CS)
CS4: R12.1, U4.4 (~CS), U12.4 (~CS), U20.4 (~CS), U28.4 (~CS), U36.4 (~CS), U44.4 (~CS), U52.4 (~CS), U60.4 (~CS)
CS5: R13.1, U5.4 (~CS), U13.4 (~CS), U21.4 (~CS), U29.4 (~CS), U37.4 (~CS), U45.4 (~CS), U53.4 (~CS), U61.4 (~CS)
CS6: R14.1, U6.4 (~CS), U14.4 (~CS), U22.4 (~CS), U30.4 (~CS), U38.4 (~CS), U46.4 (~CS), U54.4 (~CS), U62.4 (~CS)
CS7: R15.1, U7.4 (~CS), U15.4 (~CS), U23.4 (~CS), U31.4 (~CS), U39.4 (~CS), U47.4 (~CS), U55.4 (~CS), U63.4 (~CS)
CS8: R16.1, U8.4 (~CS), U16.4 (~CS), U24.4 (~CS), U32.4 (~CS), U40.4 (~CS), U48.4 (~CS), U56.4 (~CS), U64.4 (~CS)
GND: C1.2, C2.2, C3.2, C4.2, C5.2, C6.2, C7.2, C8.2, C9.2, C10.2, C11.2, C12.2, C13.2, C14.2, C15.2, C16.2, C17.2, C18.2, C19.2, C20.2, C21.2, C22.2, C23.2, C24.2, C25.2, C26.2, C27.2, C28.2, C29.2, C30.2, C31.2, C32.2, C33.2, C34.2, C35.2, C36.2, C37.2, C38.2, C39.2, C40.2, C41.2, C42.2, C43.2, C44.2, C45.2, C46.2, C47.2, C48.2, C49.2, C50.2, C51.2, C52.2, C53.2, C54.2, C55.2, C56.2, C57.2, C58.2, C59.2, C60.2, C61.2, C62.2, C63.2, C64.2, C65.2, C66.2, J1.1, J1.2, J1.3, J1.4, J1.5, J1.6, J1.7, J1.8, J1.9, J1.10, J1.31, J1.32, J2.21, J2.22, J2.23, J2.24, J2.25, J2.27, J2.29, J2.30, J2.31, J2.32, TP6.1, TP8.1, U1.6 (GND), U1.7 (TEST), U2.6 (GND), U2.7 (TEST), U3.6 (GND), U3.7 (TEST), U4.6 (GND), U4.7 (TEST), U5.6 (GND), U5.7 (TEST), U6.6 (GND), U6.7 (TEST), U7.6 (GND), U7.7 (TEST), U8.6 (GND), U8.7 (TEST), U9.6 (GND), U9.7 (TEST), U10.6 (GND), U10.7 (TEST), U11.6 (GND), U11.7 (TEST), U12.6 (GND), U12.7 (TEST), U13.6 (GND), U13.7 (TEST), U14.6 (GND), U14.7 (TEST), U15.6 (GND), U15.7 (TEST), U16.6 (GND), U16.7 (TEST), U17.6 (GND), U17.7 (TEST), U18.6 (GND), U18.7 (TEST), U19.6 (GND), U19.7 (TEST), U20.6 (GND), U20.7 (TEST), U21.6 (GND), U21.7 (TEST), U22.6 (GND), U22.7 (TEST), U23.6 (GND), U23.7 (TEST), U24.6 (GND), U24.7 (TEST), U25.6 (GND), U25.7 (TEST), U26.6 (GND), U26.7 (TEST), U27.6 (GND), U27.7 (TEST), U28.6 (GND), U28.7 (TEST), U29.6 (GND), U29.7 (TEST), U30.6 (GND), U30.7 (TEST), U31.6 (GND), U31.7 (TEST), U32.6 (GND), U32.7 (TEST), U33.6 (GND), U33.7 (TEST), U34.6 (GND), U34.7 (TEST), U35.6 (GND), U35.7 (TEST), U36.6 (GND), U36.7 (TEST), U37.6 (GND), U37.7 (TEST), U38.6 (GND), U38.7 (TEST), U39.6 (GND), U39.7 (TEST), U40.6 (GND), U40.7 (TEST), U41.6 (GND), U41.7 (TEST), U42.6 (GND), U42.7 (TEST), U43.6 (GND), U43.7 (TEST), U44.6 (GND), U44.7 (TEST), U45.6 (GND), U45.7 (TEST), U46.6 (GND), U46.7 (TEST), U47.6 (GND), U47.7 (TEST), U48.6 (GND), U48.7 (TEST), U49.6 (GND), U49.7 (TEST), U50.6 (GND), U50.7 (TEST), U51.6 (GND), U51.7 (TEST), U52.6 (GND), U52.7 (TEST), U53.6 (GND), U53.7 (TEST), U54.6 (GND), U54.7 (TEST), U55.6 (GND), U55.7 (TEST), U56.6 (GND), U56.7 (TEST), U57.6 (GND), U57.7 (TEST), U58.6 (GND)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
INT1: J1.30, R1.2, U1.8 (~ALERT), U2.8 (~ALERT), U3.8 (~ALERT), U4.8 (~ALERT), U5.8 (~ALERT), U6.8 (~ALERT), U7.8 (~ALERT), U8.8 (~ALERT)
INT2: J1.26, R2.2, U9.8 (~ALERT), U10.8 (~ALERT), U11.8 (~ALERT), U12.8 (~ALERT), U13.8 (~ALERT), U14.8 (~ALERT), U15.8 (~ALERT), U16.8 (~ALERT)
INT3: J1.22, R3.2, U17.8 (~ALERT), U18.8 (~ALERT), U19.8 (~ALERT), U20.8 (~ALERT), U21.8 (~ALERT), U22.8 (~ALERT), U23.8 (~ALERT), U24.8 (~ALERT)
INT4: J1.18, R4.2, U25.8 (~ALERT), U26.8 (~ALERT), U27.8 (~ALERT), U28.8 (~ALERT), U29.8 (~ALERT), U30.8 (~ALERT), U31.8 (~ALERT), U32.8 (~ALERT)
INT5: J1.14, R5.2, U33.8 (~ALERT), U34.8 (~ALERT), U35.8 (~ALERT), U36.8 (~ALERT), U37.8 (~ALERT), U38.8 (~ALERT), U39.8 (~ALERT), U40.8 (~ALERT)
INT6: J2.9, R6.2, U41.8 (~ALERT), U42.8 (~ALERT), U43.8 (~ALERT), U44.8 (~ALERT), U45.8 (~ALERT), U46.8 (~ALERT), U47.8 (~ALERT), U48.8 (~ALERT)
INT7: J2.13, R7.2, TP1.1, U49.8 (~ALERT), U50.8 (~ALERT), U51.8 (~ALERT), U52.8 (~ALERT), U53.8 (~ALERT), U54.8 (~ALERT), U55.8 (~ALERT), U56.8 (~ALERT)
INT8: J2.17, R8.2, U57.8 (~ALERT), U58.8 (~ALERT), U59.8 (~ALERT), U60.8 (~ALERT), U61.8 (~ALERT), U62.8 (~ALERT), U63.8 (~ALERT), U64.8 (~ALERT)
MISO1: J1.27, U1.3 (MISO), U2.3 (MISO), U3.3 (MISO), U4.3 (MISO), U5.3 (MISO), U6.3 (MISO), U7.3 (MISO), U8.3 (MISO)
MISO2: J1.23, U9.3 (MISO), U10.3 (MISO), U11.3 (MISO), U12.3 (MISO), U13.3 (MISO), U14.3 (MISO), U15.3 (MISO), U16.3 (MISO)
MISO3: J1.19, U17.3 (MISO), U18.3 (MISO), U19.3 (MISO), U20.3 (MISO), U21.3 (MISO), U22.3 (MISO), U23.3 (MISO), U24.3 (MISO)
MISO4: J1.15, U25.3 (MISO), U26.3 (MISO), U27.3 (MISO), U28.3 (MISO), U29.3 (MISO), U30.3 (MISO), U31.3 (MISO), U32.3 (MISO)
MISO5: J1.11, U33.3 (MISO), U34.3 (MISO), U35.3 (MISO), U36.3 (MISO), U37.3 (MISO), U38.3 (MISO), U39.3 (MISO), U40.3 (MISO)
MISO6: J2.12, U41.3 (MISO), U42.3 (MISO), U43.3 (MISO), U44.3 (MISO), U45.3 (MISO), U46.3 (MISO), U47.3 (MISO), U48.3 (MISO)
MISO7: J2.16, TP4.1, U49.3 (MISO), U50.3 (MISO), U51.3 (MISO), U52.3 (MISO), U53.3 (MISO), U54.3 (MISO), U55.3 (MISO), U56.3 (MISO)
MISO8: J2.20, U57.3 (MISO), U58.3 (MISO), U59.3 (MISO), U60.3 (MISO), U61.3 (MISO), U62.3 (MISO), U63.3 (MISO), U64.3 (MISO)
MOSI1: J1.28, U1.2 (MOSI), U2.2 (MOSI), U3.2 (MOSI), U4.2 (MOSI), U5.2 (MOSI), U6.2 (MOSI), U7.2 (MOSI), U8.2 (MOSI)
MOSI2: J1.24, U9.2 (MOSI), U10.2 (MOSI), U11.2 (MOSI), U12.2 (MOSI), U13.2 (MOSI), U14.2 (MOSI), U15.2 (MOSI), U16.2 (MOSI)
MOSI3: J1.20, U17.2 (MOSI), U18.2 (MOSI), U19.2 (MOSI), U20.2 (MOSI), U21.2 (MOSI), U22.2 (MOSI), U23.2 (MOSI), U24.2 (MOSI)
MOSI4: J1.16, U25.2 (MOSI), U26.2 (MOSI), U27.2 (MOSI), U28.2 (MOSI), U29.2 (MOSI), U30.2 (MOSI), U31.2 (MOSI), U32.2 (MOSI)
MOSI5: J1.12, U33.2 (MOSI), U34.2 (MOSI), U35.2 (MOSI), U36.2 (MOSI), U37.2 (MOSI), U38.2 (MOSI), U39.2 (MOSI), U40.2 (MOSI)
MOSI6: J2.11, U41.2 (MOSI), U42.2 (MOSI), U43.2 (MOSI), U44.2 (MOSI), U45.2 (MOSI), U46.2 (MOSI), U47.2 (MOSI), U48.2 (MOSI)
MOSI7: J2.15, TP3.1, U49.2 (MOSI), U50.2 (MOSI), U51.2 (MOSI), U52.2 (MOSI), U53.2 (MOSI), U54.2 (MOSI), U55.2 (MOSI), U56.2 (MOSI)
MOSI8: J2.19, U57.2 (MOSI), U58.2 (MOSI), U59.2 (MOSI), U60.2 (MOSI), U61.2 (MOSI), U62.2 (MOSI), U63.2 (MOSI), U64.2 (MOSI)
unnamed: J2.1, R16.2
unnamed: J2.2, R15.2
unnamed: J2.3, R14.2
unnamed: J2.4, R13.2
unnamed: J2.5, R12.2
unnamed: J2.6, R11.2
unnamed: J2.7, R10.2
unnamed: J2.8, R9.2
SCLK1: J1.29, U1.1 (SCLK), U2.1 (SCLK), U3.1 (SCLK), U4.1 (SCLK), U5.1 (SCLK), U6.1 (SCLK), U7.1 (SCLK), U8.1 (SCLK)
SCLK2: J1.25, U9.1 (SCLK), U10.1 (SCLK), U11.1 (SCLK), U12.1 (SCLK), U13.1 (SCLK), U14.1 (SCLK), U15.1 (SCLK), U16.1 (SCLK)
SCLK3: J1.21, U17.1 (SCLK), U18.1 (SCLK), U19.1 (SCLK), U20.1 (SCLK), U21.1 (SCLK), U22.1 (SCLK), U23.1 (SCLK), U24.1 (SCLK)
SCLK4: J1.17, U25.1 (SCLK), U26.1 (SCLK), U27.1 (SCLK), U28.1 (SCLK), U29.1 (SCLK), U30.1 (SCLK), U31.1 (SCLK), U32.1 (SCLK)
SCLK5: J1.13, U33.1 (SCLK), U34.1 (SCLK), U35.1 (SCLK), U36.1 (SCLK), U37.1 (SCLK), U38.1 (SCLK), U39.1 (SCLK), U40.1 (SCLK)
SCLK6: J2.10, U41.1 (SCLK), U42.1 (SCLK), U43.1 (SCLK), U44.1 (SCLK), U45.1 (SCLK), U46.1 (SCLK), U47.1 (SCLK), U48.1 (SCLK)
SCLK7: J2.14, TP2.1, U49.1 (SCLK), U50.1 (SCLK), U51.1 (SCLK), U52.1 (SCLK), U53.1 (SCLK), U54.1 (SCLK), U55.1 (SCLK), U56.1 (SCLK)
SCLK8: J2.18, U57.1 (SCLK), U58.1 (SCLK), U59.1 (SCLK), U60.1 (SCLK), U61.1 (SCLK), U62.1 (SCLK), U63.1 (SCLK), U64.1 (SCLK)
VCC: C1.1, C2.1, C3.1, C4.1, C5.1, C6.1, C7.1, C8.1, C9.1, C10.1, C11.1, C12.1, C13.1, C14.1, C15.1, C16.1, C17.1, C18.1, C19.1, C20.1, C21.1, C22.1, C23.1, C24.1, C25.1, C26.1, C27.1, C28.1, C29.1, C30.1, C31.1, C32.1, C66.1, J2.28, R1.1, R2.1, R3.1, R4.1, TP5.1, U1.5 (VCC), U2.5 (VCC), U3.5 (VCC), U4.5 (VCC), U5.5 (VCC), U6.5 (VCC), U7.5 (VCC), U8.5 (VCC), U9.5 (VCC), U10.5 (VCC), U11.5 (VCC), U12.5 (VCC), U13.5 (VCC), U14.5 (VCC), U15.5 (VCC), U16.5 (VCC), U17.5 (VCC), U18.5 (VCC), U19.5 (VCC), U20.5 (VCC), U21.5 (VCC), U22.5 (VCC), U23.5 (VCC), U24.5 (VCC), U25.5 (VCC), U26.5 (VCC), U27.5 (VCC), U28.5 (VCC), U29.5 (VCC), U30.5 (VCC), U31.5 (VCC), U32.5 (VCC)
VCC2: C33.1, C34.1, C35.1, C36.1, C37.1, C38.1, C39.1, C40.1, C41.1, C42.1, C43.1, C44.1, C45.1, C46.1, C47.1, C48.1, C49.1, C50.1, C51.1, C52.1, C53.1, C54.1, C55.1, C56.1, C57.1, C58.1, C59.1, C60.1, C61.1, C62.1, C63.1, C64.1, C65.1, J2.26, R5.1, R6.1, R7.1, R8.1, TP7.1, U33.5 (VCC), U34.5 (VCC), U35.5 (VCC), U36.5 (VCC), U37.5 (VCC), U38.5 (VCC), U39.5 (VCC), U40.5 (VCC), U41.5 (VCC), U42.5 (VCC), U43.5 (VCC), U44.5 (VCC), U45.5 (VCC), U46.5 (VCC), U47.5 (VCC), U48.5 (VCC), U49.5 (VCC), U50.5 (VCC), U51.5 (VCC), U52.5 (VCC), U53.5 (VCC), U54.5 (VCC), U55.5 (VCC), U56.5 (VCC), U57.5 (VCC), U58.5 (VCC), U59.5 (VCC), U60.5 (VCC), U61.5 (VCC), U62.5 (VCC), U63.5 (VCC), U64.5 (VCC)

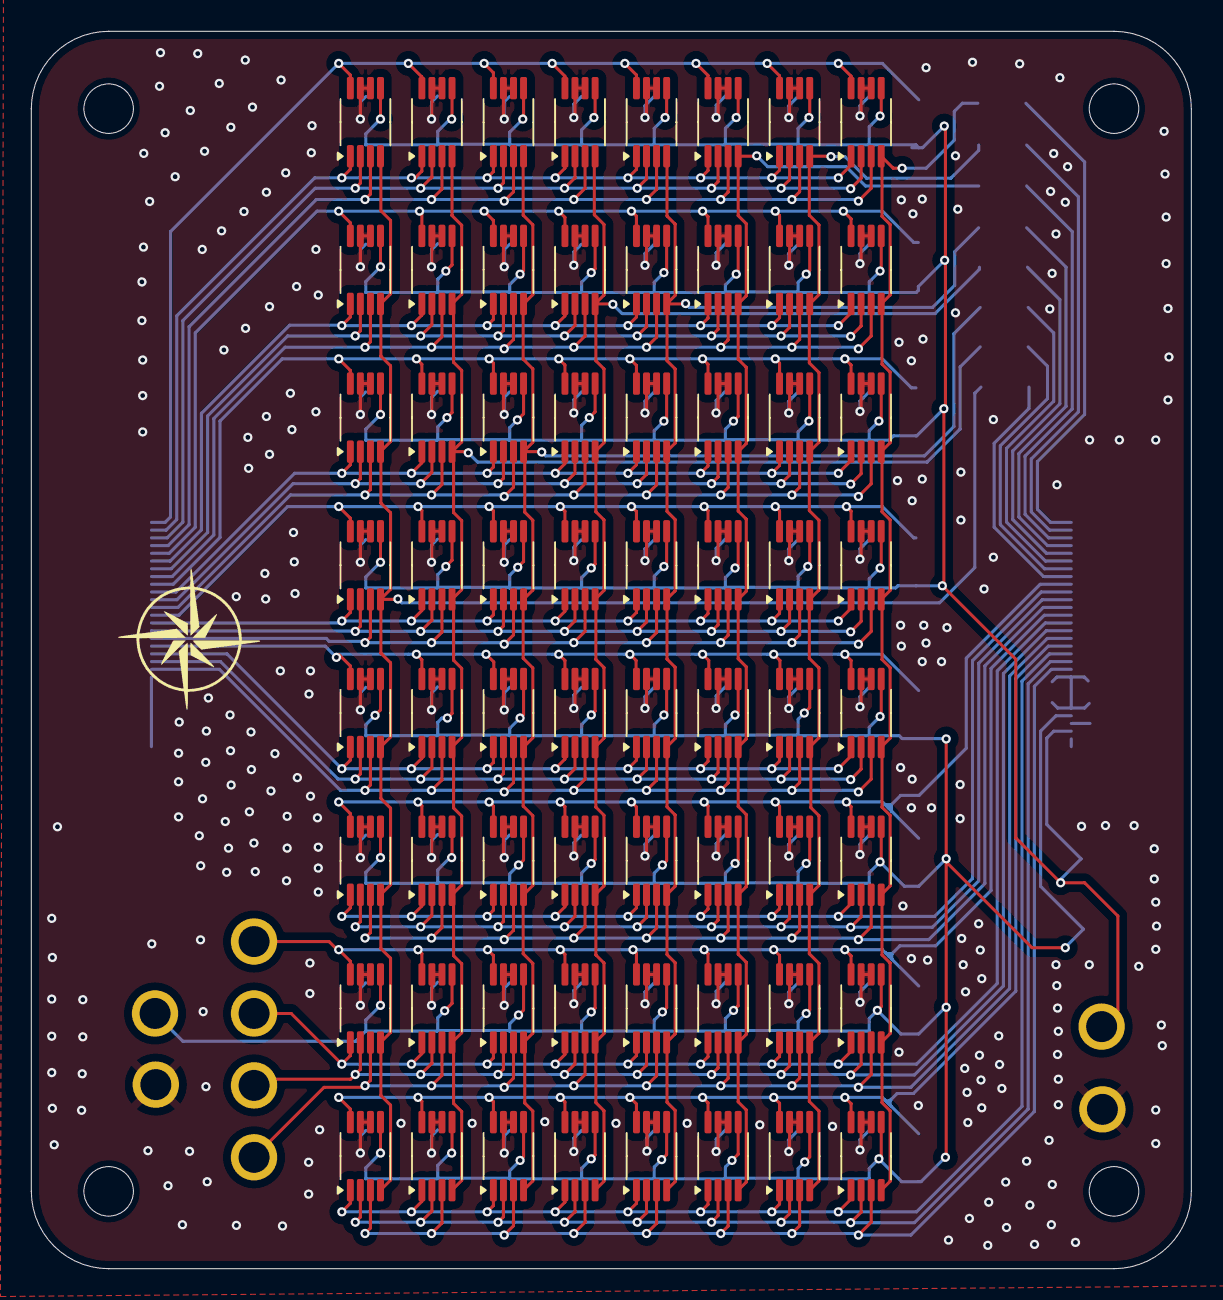
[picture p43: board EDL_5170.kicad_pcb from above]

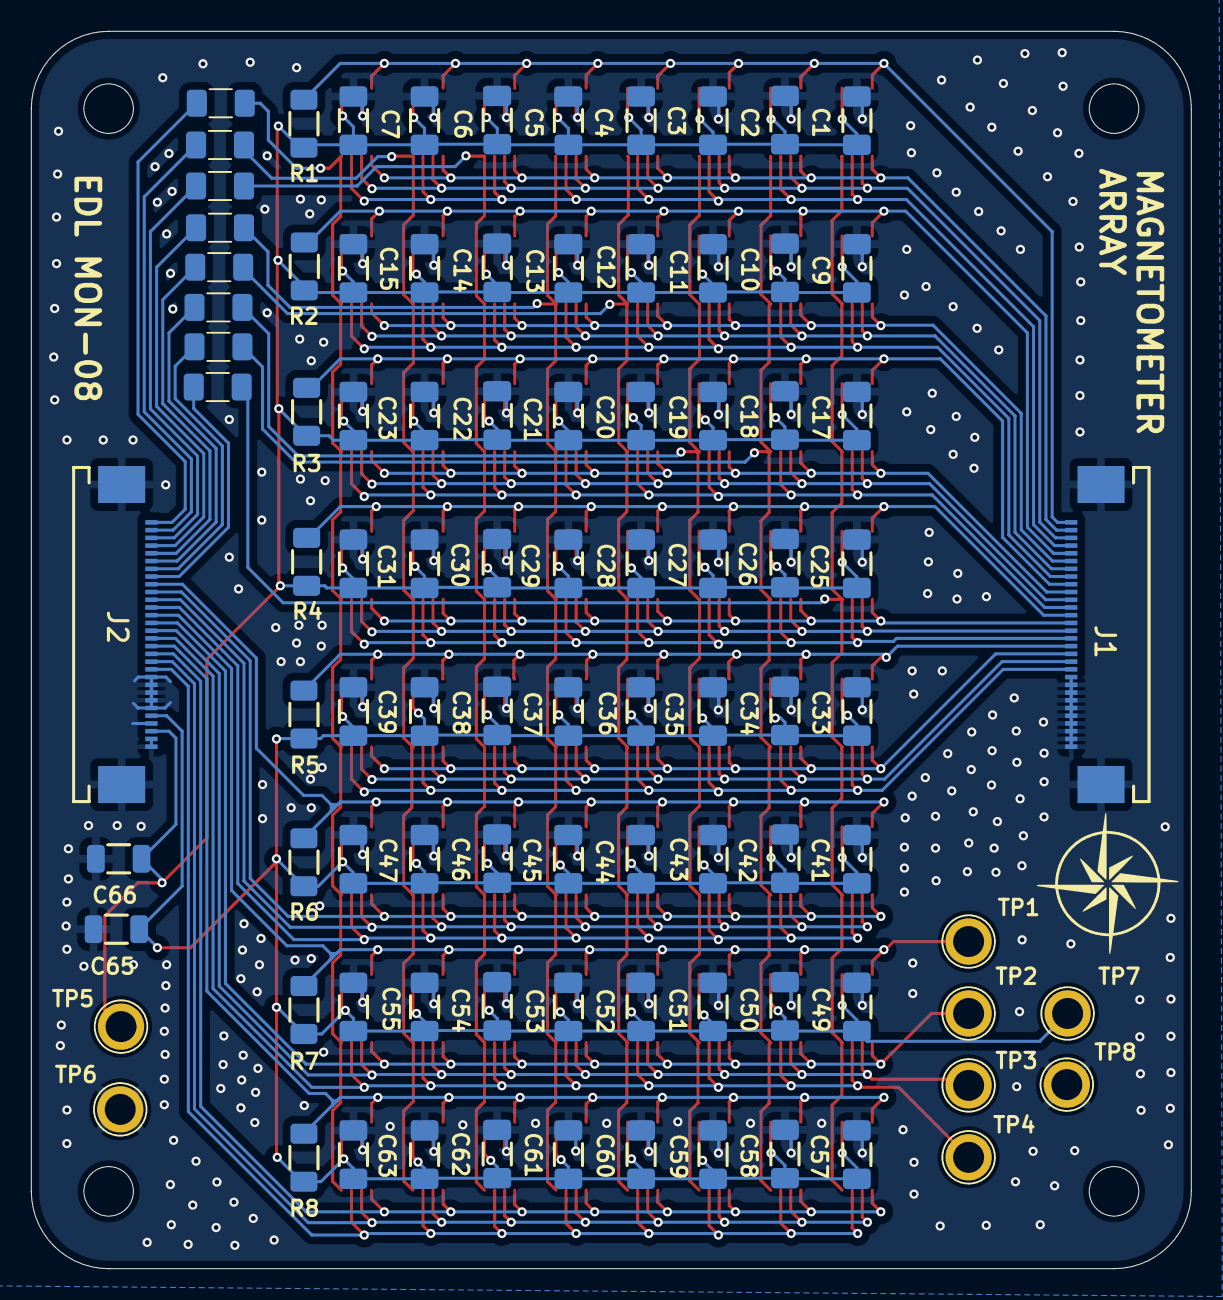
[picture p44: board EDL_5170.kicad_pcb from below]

Board: 2 copper layers, 75.0 x 80.0 mm, 156 parts (92 on the bottom side), 51 nets.

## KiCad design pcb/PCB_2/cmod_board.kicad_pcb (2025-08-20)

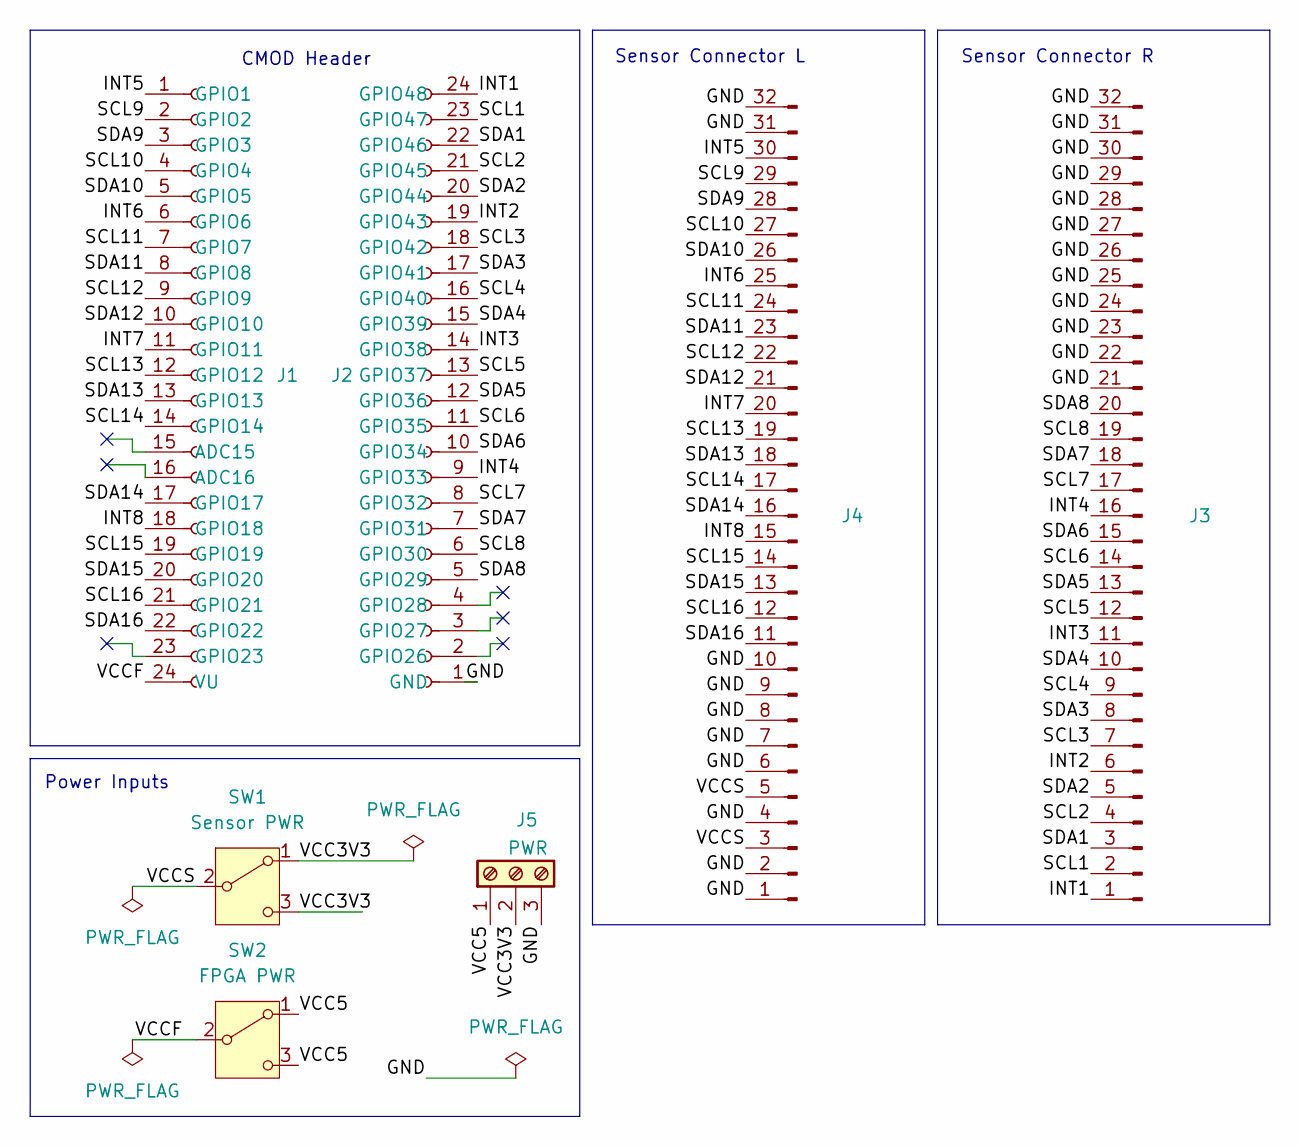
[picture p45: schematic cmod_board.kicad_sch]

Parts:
J1: PinSocket_1x24_P2.54mm_Vertical
J2: Conn_01x24_Socket; PinSocket_1x24_P2.54mm_Vertical
J3, J4: Conn_01x32_Pin; 52435-3071
J5: PWR; TerminalBlock_Phoenix_PT-1,5-3-3.5-H_1x03_P3.50mm_Horizontal
SW1: Sensor PWR; SPDT Switch 3 mm
SW2: FPGA PWR; SPDT Switch 3 mm

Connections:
/GND: J2.1 (GND), J3.21, J3.22, J3.23, J3.24, J3.25, J3.26, J3.27, J3.28, J3.29, J3.30, J3.31, J3.32, J4.1, J4.2, J4.4, J4.6, J4.7, J4.8, J4.9, J4.10, J4.31, J4.32, J5.3
/INT1: J2.24 (GPIO48), J3.1
/INT2: J2.19 (GPIO43), J3.6
/INT3: J2.14 (GPIO38), J3.11
/INT4: J2.9 (GPIO33), J3.16
/INT5: J1.1 (GPIO1), J4.30
/INT6: J1.6 (GPIO6), J4.25
/INT7: J1.11 (GPIO11), J4.20
/INT8: J1.18 (GPIO18), J4.15
/SCL1: J2.23 (GPIO47), J3.2
/SCL2: J2.21 (GPIO45), J3.4
/SCL3: J2.18 (GPIO42), J3.7
/SCL4: J2.16 (GPIO40), J3.9
/SCL5: J2.13 (GPIO37), J3.12
/SCL6: J2.11 (GPIO35), J3.14
/SCL7: J2.8 (GPIO32), J3.17
/SCL8: J2.6 (GPIO30), J3.19
/SCL9: J1.2 (GPIO2), J4.29
/SCL10: J1.4 (GPIO4), J4.27
/SCL11: J1.7 (GPIO7), J4.24
/SCL12: J1.9 (GPIO9), J4.22
/SCL13: J1.12 (GPIO12), J4.19
/SCL14: J1.14 (GPIO14), J4.17
/SCL15: J1.19 (GPIO19), J4.14
/SCL16: J1.21 (GPIO21), J4.12
/SDA1: J2.22 (GPIO46), J3.3
/SDA2: J2.20 (GPIO44), J3.5
/SDA3: J2.17 (GPIO41), J3.8
/SDA4: J2.15 (GPIO39), J3.10
/SDA5: J2.12 (GPIO36), J3.13
/SDA6: J2.10 (GPIO34), J3.15
/SDA7: J2.7 (GPIO31), J3.18
/SDA8: J2.5 (GPIO29), J3.20
/SDA9: J1.3 (GPIO3), J4.28
/SDA10: J1.5 (GPIO5), J4.26
/SDA11: J1.8 (GPIO8), J4.23
/SDA12: J1.10 (GPIO10), J4.21
/SDA13: J1.13 (GPIO13), J4.18
/SDA14: J1.17 (GPIO17), J4.16
/SDA15: J1.20 (GPIO20), J4.13
/SDA16: J1.22 (GPIO22), J4.11
/VCC3V3: J5.2, SW1.1 (A), SW1.3 (C)
/VCC5: J5.1, SW2.1 (A), SW2.3 (C)
/VCCF: J1.24 (VU), SW2.2 (B)
/VCCS: J4.3, J4.5, SW1.2 (B)

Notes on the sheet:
CMOD Header
Sensor Connector R
Sensor Connector L
Power Inputs

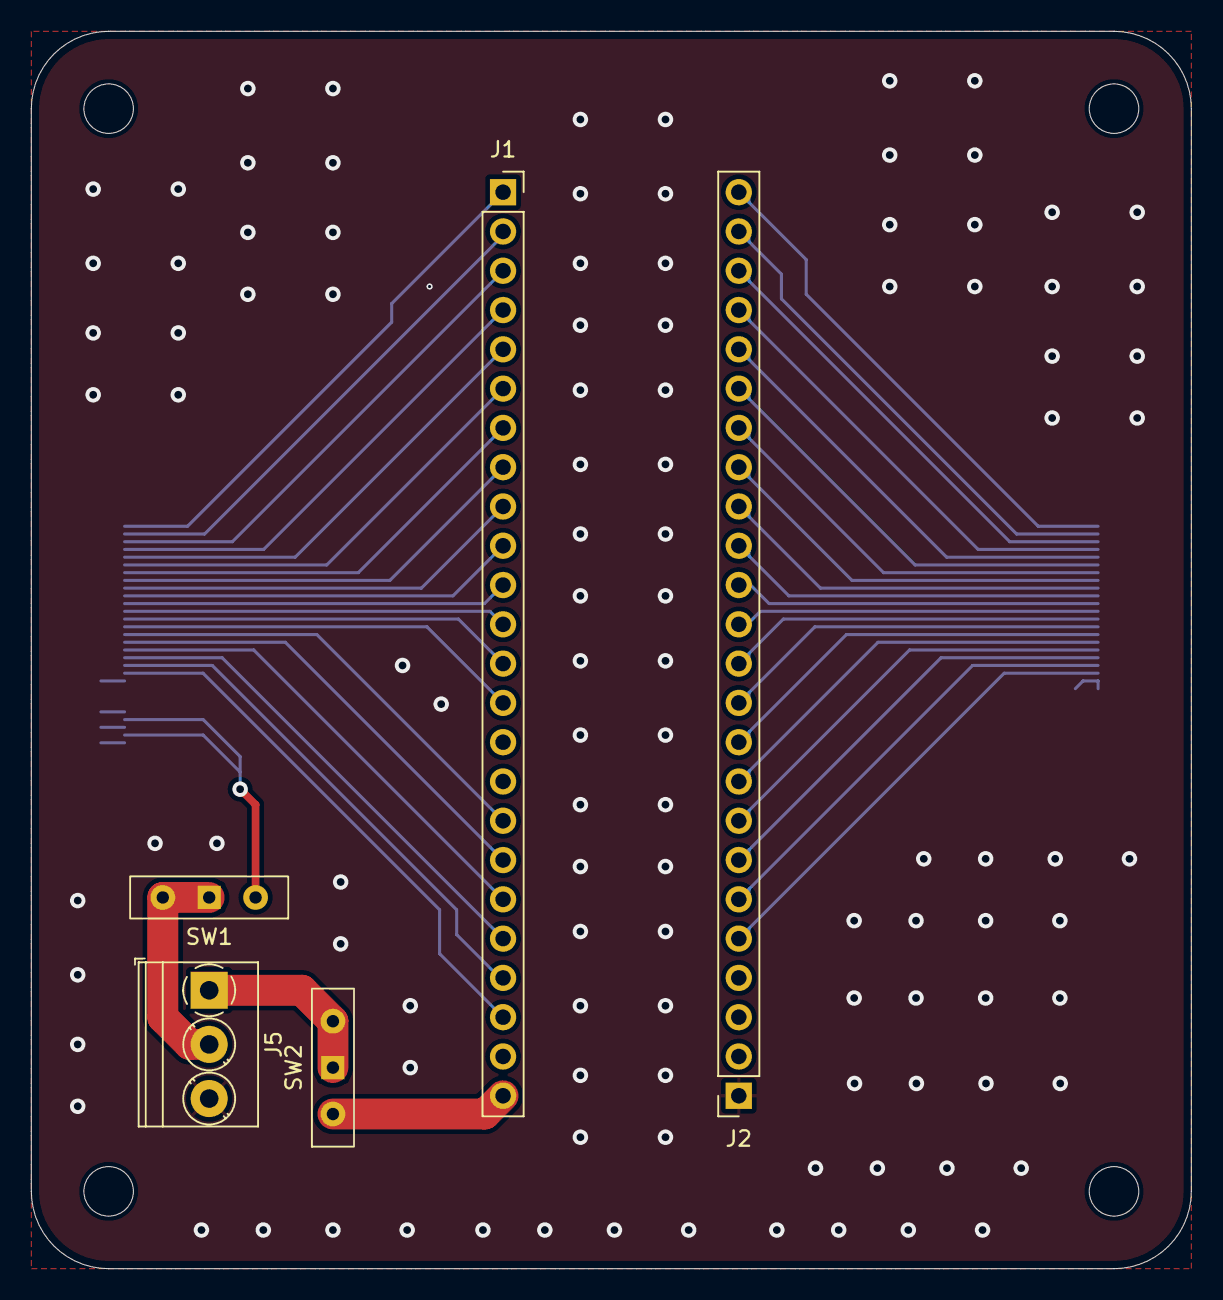
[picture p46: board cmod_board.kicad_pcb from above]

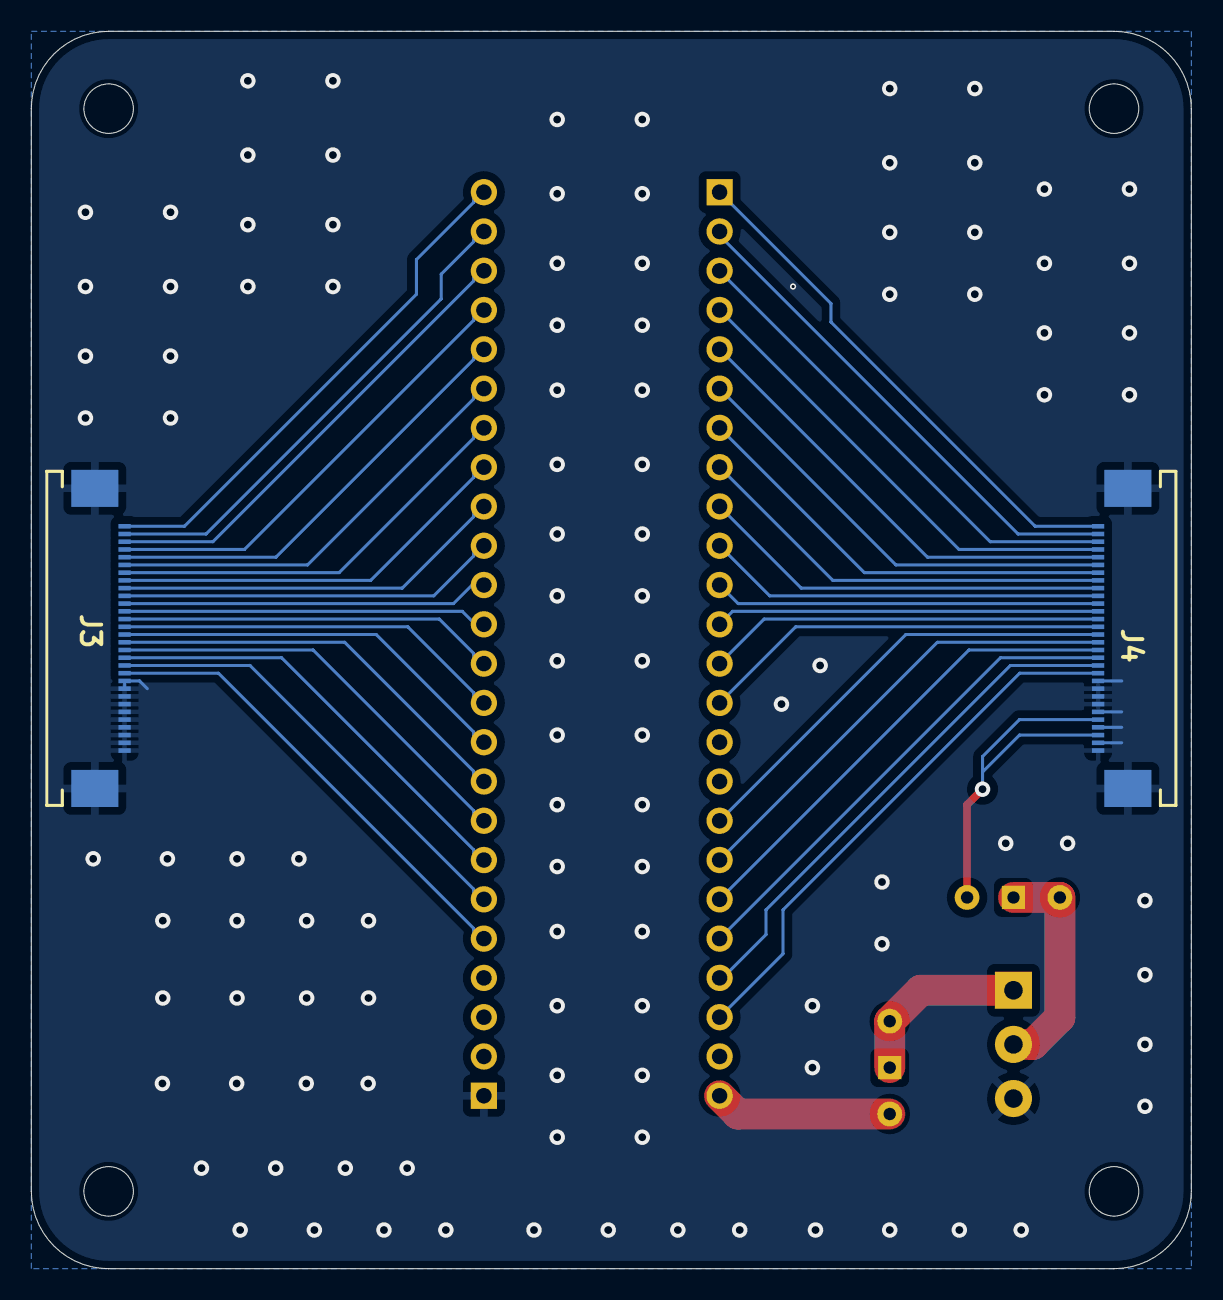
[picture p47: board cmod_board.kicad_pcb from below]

Board: 2 copper layers, 75.0 x 80.0 mm, 7 parts (2 on the bottom side), 45 nets.

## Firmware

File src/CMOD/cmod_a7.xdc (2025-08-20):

## XDC File for CMOD A7.
## The appropriate GPIO Pins have been uncommented.
set_property CFGBVS VCCO [current_design]
set_property CONFIG_VOLTAGE 3.3 [current_design]
## 12 MHz Clock Signal
set_property -dict {PACKAGE_PIN L17 IOSTANDARD LVCMOS33} [get_ports sys_clk]


## LEDs
set_property -dict {PACKAGE_PIN A17 IOSTANDARD LVCMOS33} [get_ports rst_status]
#set_property -dict { PACKAGE_PIN C16   IOSTANDARD LVCMOS33 } [get_ports { buff_status }]; #IO_L13P_T2_MRCC_16 Sch=led[2]

## RGB LED
#set_property -dict { PACKAGE_PIN B17   IOSTANDARD LVCMOS33 } [get_ports { led0_b }]; #IO_L14N_T2_SRCC_16 Sch=led0_b
#set_property -dict { PACKAGE_PIN B16   IOSTANDARD LVCMOS33 } [get_ports { led0_g }]; #IO_L13N_T2_MRCC_16 Sch=led0_g
#set_property -dict { PACKAGE_PIN C17   IOSTANDARD LVCMOS33 } [get_ports { led0_r }]; #IO_L14P_T2_SRCC_16 Sch=led0_r

## Buttons
set_property -dict {PACKAGE_PIN A18 IOSTANDARD LVCMOS33} [get_ports reset]
#set_property -dict { PACKAGE_PIN B18   IOSTANDARD LVCMOS33 } [get_ports { trig }]; #IO_L19P_T3_16 Sch=btn[1]

## Pmod Header JA
#set_property -dict {PACKAGE_PIN G17 IOSTANDARD LVCMOS33} [get_ports spi_mosi]
#set_property -dict {PACKAGE_PIN G19 IOSTANDARD LVCMOS33} [get_ports spi_sck]
#set_property -dict {PACKAGE_PIN N18 IOSTANDARD LVCMOS33} [get_ports spi_miso]
#set_property -dict {PACKAGE_PIN L18 IOSTANDARD LVCMOS33} [get_ports spi_cs]
set_property -dict { PACKAGE_PIN H17   IOSTANDARD LVCMOS33 } [get_ports { spi_mosi }]; #IO_L5P_T0_D06_14 Sch=ja[7]
set_property -dict { PACKAGE_PIN H19   IOSTANDARD LVCMOS33 } [get_ports { spi_clk }]; #IO_L4P_T0_D04_14 Sch=ja[8]
set_property -dict { PACKAGE_PIN J19   IOSTANDARD LVCMOS33 } [get_ports { spi_miso }]; #IO_L6N_T0_D08_VREF_14 Sch=ja[9]
set_property -dict { PACKAGE_PIN K18   IOSTANDARD LVCMOS33 } [get_ports { spi_cs }]; #IO_L8N_T1_D12_14 Sch=ja[10]
create_clock -add -name spi_clk -period 100.00 -waveform {0 50.00} [get_ports {spi_clk}];
## Analog XADC Pins
## Only declare these if you want to use pins 15 and 16 as single ended analog inputs. pin 15 -> vaux4, pin16 -> vaux12
#set_property -dict { PACKAGE_PIN G2    IOSTANDARD LVCMOS33 } [get_ports { xa_n[0] }]; #IO_L1N_T0_AD4N_35 Sch=ain_n[15]
#set_property -dict { PACKAGE_PIN G3    IOSTANDARD LVCMOS33 } [get_ports { xa_p[0] }]; #IO_L1P_T0_AD4P_35 Sch=ain_p[15]
#set_property -dict { PACKAGE_PIN J2    IOSTANDARD LVCMOS33 } [get_ports { xa_n[1] }]; #IO_L2N_T0_AD12N_35 Sch=ain_n[16]
#set_property -dict { PACKAGE_PIN H2    IOSTANDARD LVCMOS33 } [get_ports { xa_p[1] }]; #IO_L2P_T0_AD12P_35 Sch=ain_p[16]

## GPIO Pins
## Pins 15 and 16 should remain commented if using them as analog inputs
set_property -dict {PACKAGE_PIN M3 IOSTANDARD LVCMOS33} [get_ports {int[1]}]
set_property -dict {PACKAGE_PIN L3 IOSTANDARD LVCMOS33} [get_ports {scl[1]}]
set_property -dict {PACKAGE_PIN A16 IOSTANDARD LVCMOS33} [get_ports {sda[1]}]
set_property -dict {PACKAGE_PIN K3 IOSTANDARD LVCMOS33} [get_ports {scl[3]}]
set_property -dict {PACKAGE_PIN C15 IOSTANDARD LVCMOS33} [get_ports {sda[3]}]
set_property -dict {PACKAGE_PIN H1 IOSTANDARD LVCMOS33} [get_ports {int[3]}]
set_property -dict {PACKAGE_PIN A15 IOSTANDARD LVCMOS33} [get_ports {scl[5]}]
set_property -dict {PACKAGE_PIN B15 IOSTANDARD LVCMOS33} [get_ports {sda[5]}]
set_property -dict {PACKAGE_PIN A14 IOSTANDARD LVCMOS33} [get_ports {scl[7]}]
set_property -dict {PACKAGE_PIN J3 IOSTANDARD LVCMOS33} [get_ports {sda[7]}]
set_property -dict {PACKAGE_PIN J1 IOSTANDARD LVCMOS33} [get_ports {int[5]}]
set_property -dict {PACKAGE_PIN K2 IOSTANDARD LVCMOS33} [get_ports {scl[9]}]
set_property -dict {PACKAGE_PIN L1 IOSTANDARD LVCMOS33} [get_ports {sda[9]}]
set_property -dict {PACKAGE_PIN L2 IOSTANDARD LVCMOS33} [get_ports {scl[11]}]
set_property -dict {PACKAGE_PIN M1 IOSTANDARD LVCMOS33} [get_ports {sda[11]}]
set_property -dict {PACKAGE_PIN N3 IOSTANDARD LVCMOS33} [get_ports {int[7]}]
set_property -dict {PACKAGE_PIN P3 IOSTANDARD LVCMOS33} [get_ports {scl[13]}]
set_property -dict {PACKAGE_PIN M2 IOSTANDARD LVCMOS33} [get_ports {sda[13]}]
set_property -dict {PACKAGE_PIN N1 IOSTANDARD LVCMOS33} [get_ports {scl[15]}]
set_property -dict {PACKAGE_PIN N2 IOSTANDARD LVCMOS33} [get_ports {sda[15]}]
#set_property -dict { PACKAGE_PIN P1    IOSTANDARD LVCMOS33 } [get_ports { pio23 }]; #IO_L19N_T3_VREF_35 Sch=pio[23]
#set_property -dict { PACKAGE_PIN R3    IOSTANDARD LVCMOS33 } [get_ports { pio26 }]; #IO_L2P_T0_34 Sch=pio[26]
#set_property -dict { PACKAGE_PIN T3    IOSTANDARD LVCMOS33 } [get_ports { pio27 }]; #IO_L2N_T0_34 Sch=pio[27]
#set_property -dict { PACKAGE_PIN R2    IOSTANDARD LVCMOS33 } [get_ports { pio28 }]; #IO_L1P_T0_34 Sch=pio[28]
set_property -dict {PACKAGE_PIN T1 IOSTANDARD LVCMOS33} [get_ports {sda[14]}]
set_property -dict {PACKAGE_PIN T2 IOSTANDARD LVCMOS33} [get_ports {scl[14]}]
set_property -dict {PACKAGE_PIN U1 IOSTANDARD LVCMOS33} [get_ports {sda[12]}]
set_property -dict {PACKAGE_PIN W2 IOSTANDARD LVCMOS33} [get_ports {scl[12]}]
set_property -dict {PACKAGE_PIN V2 IOSTANDARD LVCMOS33} [get_ports {int[6]}]
set_property -dict {PACKAGE_PIN W3 IOSTANDARD LVCMOS33} [get_ports {sda[10]}]
set_property -dict {PACKAGE_PIN V3 IOSTANDARD LVCMOS33} [get_ports {scl[10]}]
set_property -dict {PACKAGE_PIN W5 IOSTANDARD LVCMOS33} [get_ports {sda[8]}]
set_property -dict {PACKAGE_PIN V4 IOSTANDARD LVCMOS33} [get_ports {scl[8]}]
set_property -dict {PACKAGE_PIN U4 IOSTANDARD LVCMOS33} [get_ports {int[4]}]
set_property -dict {PACKAGE_PIN V5 IOSTANDARD LVCMOS33} [get_ports {sda[6]}]
set_property -dict {PACKAGE_PIN W4 IOSTANDARD LVCMOS33} [get_ports {scl[6]}]
set_property -dict {PACKAGE_PIN U5 IOSTANDARD LVCMOS33} [get_ports {sda[4]}]
set_property -dict {PACKAGE_PIN U2 IOSTANDARD LVCMOS33} [get_ports {scl[4]}]
set_property -dict {PACKAGE_PIN W6 IOSTANDARD LVCMOS33} [get_ports {int[2]}]
set_property -dict {PACKAGE_PIN U3 IOSTANDARD LVCMOS33} [get_ports {sda[2]}]
set_property -dict {PACKAGE_PIN U7 IOSTANDARD LVCMOS33} [get_ports {scl[2]}]
set_property -dict {PACKAGE_PIN W7 IOSTANDARD LVCMOS33} [get_ports {sda[0]}]
set_property -dict {PACKAGE_PIN U8 IOSTANDARD LVCMOS33} [get_ports {scl[0]}]
set_property -dict {PACKAGE_PIN V8 IOSTANDARD LVCMOS33} [get_ports {int[0]}]

## UART
#set_property -dict { PACKAGE_PIN J18   IOSTANDARD LVCMOS33 } [get_ports { tx_out }]; #IO_L7N_T1_D10_14 Sch=uart_rxd_out
#set_property -dict { PACKAGE_PIN J17   IOSTANDARD LVCMOS33 } [get_ports { rx_in }]; #IO_L7P_T1_D09_14 Sch=uart_txd_in

## Crypto 1 Wire Interface
#set_property -dict { PACKAGE_PIN D17   IOSTANDARD LVCMOS33 } [get_ports { crypto_sda }]; #IO_0_14 Sch=crypto_sda

## QSPI
#set_property -dict { PACKAGE_PIN K19   IOSTANDARD LVCMOS33 } [get_ports { qspi_cs    }]; #IO_L6P_T0_FCS_B_14 Sch=qspi_cs
#set_property -dict { PACKAGE_PIN D18   IOSTANDARD LVCMOS33 } [get_ports { qspi_dq[0] }]; #IO_L1P_T0_D00_MOSI_14 Sch=qspi_dq[0]
#set_property -dict { PACKAGE_PIN D19   IOSTANDARD LVCMOS33 } [get_ports { qspi_dq[1] }]; #IO_L1N_T0_D01_DIN_14 Sch=qspi_dq[1]
#set_property -dict { PACKAGE_PIN G18   IOSTANDARD LVCMOS33 } [get_ports { qspi_dq[2] }]; #IO_L2P_T0_D02_14 Sch=qspi_dq[2]
#set_property -dict { PACKAGE_PIN F18   IOSTANDARD LVCMOS33 } [get_ports { qspi_dq[3] }]; #IO_L2N_T0_D03_14 Sch=qspi_dq[3]

## Cellular RAM
#set_property -dict { PACKAGE_PIN M18   IOSTANDARD LVCMOS33 } [get_ports { MemAdr[0]  }]; #IO_L11P_T1_SRCC_14 Sch=sram- a[0]
#set_property -dict { PACKAGE_PIN M19   IOSTANDARD LVCMOS33 } [get_ports { MemAdr[1]  }]; #IO_L11N_T1_SRCC_14 Sch=sram- a[1]
#set_property -dict { PACKAGE_PIN K17   IOSTANDARD LVCMOS33 } [get_ports { MemAdr[2]  }]; #IO_L12N_T1_MRCC_14 Sch=sram- a[2]
#set_property -dict { PACKAGE_PIN N17   IOSTANDARD LVCMOS33 } [get_ports { MemAdr[3]  }]; #IO_L13P_T2_MRCC_14 Sch=sram- a[3]
#set_property -dict { PACKAGE_PIN P17   IOSTANDARD LVCMOS33 } [get_ports { MemAdr[4]  }]; #IO_L13N_T2_MRCC_14 Sch=sram- a[4]
#set_property -dict { PACKAGE_PIN P18   IOSTANDARD LVCMOS33 } [get_ports { MemAdr[5]  }]; #IO_L14P_T2_SRCC_14 Sch=sram- a[5]
#set_property -dict { PACKAGE_PIN R18   IOSTANDARD LVCMOS33 } [get_ports { MemAdr[6]  }]; #IO_L14N_T2_SRCC_14 Sch=sram- a[6]
#set_property -dict { PACKAGE_PIN W19   IOSTANDARD LVCMOS33 } [get_ports { MemAdr[7]  }]; #IO_L16N_T2_A15_D31_14 Sch=sram- a[7]
#set_property -dict { PACKAGE_PIN U19   IOSTANDARD LVCMOS33 } [get_ports { MemAdr[8]  }]; #IO_L15P_T2_DQS_RDWR_B_14 Sch=sram- a[8]
#set_property -dict { PACKAGE_PIN V19   IOSTANDARD LVCMOS33 } [get_ports { MemAdr[9]  }]; #IO_L15N_T2_DQS_DOUT_CSO_B_14 Sch=sram- a[9]
#set_property -dict { PACKAGE_PIN W18   IOSTANDARD LVCMOS33 } [get_ports { MemAdr[10] }]; #IO_L16P_T2_CSI_B_14 Sch=sram- a[10]
#set_property -dict { PACKAGE_PIN T17   IOSTANDARD LVCMOS33 } [get_ports { MemAdr[11] }]; #IO_L17P_T2_A14_D30_14 Sch=sram- a[11]
#set_property -dict { PACKAGE_PIN T18   IOSTANDARD LVCMOS33 } [get_ports { MemAdr[12] }]; #IO_L17N_T2_A13_D29_14 Sch=sram- a[12]
#set_property -dict { PACKAGE_PIN U17   IOSTANDARD LVCMOS33 } [get_ports { MemAdr[13] }]; #IO_L18P_T2_A12_D28_14 Sch=sram- a[13]
#set_property -dict { PACKAGE_PIN U18   IOSTANDARD LVCMOS33 } [get_ports { MemAdr[14] }]; #IO_L18N_T2_A11_D27_14 Sch=sram- a[14]
#set_property -dict { PACKAGE_PIN V16   IOSTANDARD LVCMOS33 } [get_ports { MemAdr[15] }]; #IO_L19P_T3_A10_D26_14 Sch=sram- a[15]
#set_property -dict { PACKAGE_PIN W16   IOSTANDARD LVCMOS33 } [get_ports { MemAdr[16] }]; #IO_L20P_T3_A08_D24_14 Sch=sram- a[16]
#set_property -dict { PACKAGE_PIN W17   IOSTANDARD LVCMOS33 } [get_ports { MemAdr[17] }]; #IO_L20N_T3_A07_D23_14 Sch=sram- a[17]
#set_property -dict { PACKAGE_PIN V15   IOSTANDARD LVCMOS33 } [get_ports { MemAdr[18] }]; #IO_L21P_T3_DQS_14 Sch=sram- a[18]
#set_property -dict { PACKAGE_PIN W15   IOSTANDARD LVCMOS33 } [get_ports { MemDB[0]   }]; #IO_L21N_T3_DQS_A06_D22_14 Sch=sram-dq[0]
#set_property -dict { PACKAGE_PIN W13   IOSTANDARD LVCMOS33 } [get_ports { MemDB[1]   }]; #IO_L22P_T3_A05_D21_14 Sch=sram-dq[1]
#set_property -dict { PACKAGE_PIN W14   IOSTANDARD LVCMOS33 } [get_ports { MemDB[2]   }]; #IO_L22N_T3_A04_D20_14 Sch=sram-dq[2]
#set_property -dict { PACKAGE_PIN U15   IOSTANDARD LVCMOS33 } [get_ports { MemDB[3]   }]; #IO_L23P_T3_A03_D19_14 Sch=sram-dq[3]
#set_property -dict { PACKAGE_PIN U16   IOSTANDARD LVCMOS33 } [get_ports { MemDB[4]   }]; #IO_L23N_T3_A02_D18_14 Sch=sram-dq[4]
#set_property -dict { PACKAGE_PIN V13   IOSTANDARD LVCMOS33 } [get_ports { MemDB[5]   }]; #IO_L24P_T3_A01_D17_14 Sch=sram-dq[5]
#set_property -dict { PACKAGE_PIN V14   IOSTANDARD LVCMOS33 } [get_ports { MemDB[6]   }]; #IO_L24N_T3_A00_D16_14 Sch=sram-dq[6]
#set_property -dict { PACKAGE_PIN U14   IOSTANDARD LVCMOS33 } [get_ports { MemDB[7]   }]; #IO_25_14 Sch=sram-dq[7]
#set_property -dict { PACKAGE_PIN P19   IOSTANDARD LVCMOS33 } [get_ports { RamOEn     }]; #IO_L10P_T1_D14_14 Sch=sram-oe
#set_property -dict { PACKAGE_PIN R19   IOSTANDARD LVCMOS33 } [get_ports { RamWEn     }]; #IO_L10N_T1_D15_14 Sch=sram-we
#set_property -dict { PACKAGE_PIN N19   IOSTANDARD LVCMOS33 } [get_ports { RamCEn     }]; #IO_L9N_T1_DQS_D13_14 Sch=sram-ce

## SPI Timing constraints
set_input_delay -max 8.0 -clock [get_clocks spi_clk] [get_ports spi_mosi]
set_input_delay -min 1.0 -clock [get_clocks spi_clk] [get_ports spi_mosi]
set_input_delay -max 8.0 -clock [get_clocks spi_clk] [get_ports spi_cs]
set_input_delay -min 1.0 -clock [get_clocks spi_clk] [get_ports spi_cs]
set_output_delay -max 10.0 -clock [get_clocks spi_clk] [get_ports spi_miso]
set_output_delay -min 2.0 -clock [get_clocks spi_clk] [get_ports spi_miso]


set_clock_groups -asynchronous -group [get_clocks spi_clk] -group [get_clocks sys_clk]
set_false_path -from [get_clocks spi_clk] -to [get_clocks clk_out1_clk_wiz_0]
set_false_path -from [get_clocks clk_out1_clk_wiz_0] -to [get_clocks spi_clk]


## Flash programming constraints
set_property BITSTREAM.CONFIG.CONFIGRATE 33 [current_design] 
set_property CONFIG_MODE SPIx4 [current_design]

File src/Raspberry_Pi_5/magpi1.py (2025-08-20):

import socket
import threading
import json
import time
import sys
import math
import random
import queue
import spidev
import RPi.GPIO as GPIO
from collections import deque


DATA_FILE = "data.txt"
# Simulated global queues
tcp_message_queue = queue.Queue()
udp_message_queue = queue.LifoQueue(maxsize=1000)
tcp_send_queue = queue.Queue()

# Global flags and counters
acquisition_enabled = False
running = True
n_theta = 0              # Theta motor step counter
n_r = 0                  # r motor current position (cumulative)
n_z = 0                  # Total number of steps moved in z direction
counter = 0              # Acquisition cycle counter

# Motor sweep parameters
r_count = 0
jump_count = 0
theta_jump = 1
full_revolution_theta = 200
r_jump = 4480
r_jump_half = 280
full_revolution_r = 22400
z_jump = 4480
z_jump_half = 280
full_revolution_z = 22400

acquisition_enabled = False
running = True
motor_stable_event = threading.Event()

DATA_FILE = "data.txt"

# GPIO Pin Definitions
THETA_DIR = 6 # 31
THETA_STEP = 5 # 29
R_DIR = 27 # 13
R_STEP = 17 # 11
Z_DIR = 24 # 18
Z_STEP = 23 # 16

"""
Z
True = Up (CW)
False - Down (ACW)

R
False - In (anticlockwise)
True - Out (clockwise)

Theta
False - ACW
True - CW

"""
# Directions for future reference
Z_UP = True
Z_DOWN = False
R_IN = False
R_OUT = True
THETA_CW = True
THETA_ACW = False

# Set GPIO pins
GPIO.setmode(GPIO.BCM)
GPIO.setwarnings(False)
for DIR, STEP in [(THETA_DIR, THETA_STEP), (R_DIR, R_STEP), (Z_DIR, Z_STEP)]:
    GPIO.setup(DIR, GPIO.OUT)
    GPIO.setup(STEP, GPIO.OUT)

last_file_pos = 0
file_lock = threading.Lock()

######## SPI CODE ##################
# SPI Setup
SPI_BUS = 0
SPI_DEVICE = 0
SPI_SPEED = 10000000
SPI_MODE = 3

spi = spidev.SpiDev()
spi.open(SPI_BUS, SPI_DEVICE)
spi.max_speed_hz = SPI_SPEED
spi.mode = SPI_MODE


#---------------------- SPI -----------------------------------
# Define a simulation of SPI for debugging
def simulate_spi():
    frames = []
    timestamp = int(time.time() * 1000) & 0xFF
    t = time.time()
    for pix_id in range(64):
        angle = (t * 10 + pix_id) % (2 * math.pi)
        x = int(1000 * math.sin(angle)) & 0xFFFF
        y = int(1000 * math.cos(angle)) & 0xFFFF
        z = int(1000 * math.sin(angle + math.pi / 4)) & 0xFFFF

        word0 = (pix_id & 0x7) << 28 | ((y & 0xFFF) << 16) | (x & 0xFFFF)
        word1 = (1 << 31) | ((pix_id >> 3) & 0x7) << 28 | (timestamp << 20) | ((z & 0xFFFF) << 4) | ((y >> 12) & 0xF)
        frame = (word1 << 32) | word0
        frames.append(frame)
    return frames

# Send commands via SPI to the FPGA to boot, shutdown, etc
# Send a 64-bit command to the FPGA as 8 separate 8-bit bytes in big-endian order.
def send_command(cmd):

    cmd_bytes = [
        (cmd >> 56) & 0xFF,
        (cmd >> 48) & 0xFF,
        (cmd >> 40) & 0xFF,
        (cmd >> 32) & 0xFF,
        (cmd >> 24) & 0xFF,
        (cmd >> 16) & 0xFF,
        (cmd >> 8)  & 0xFF,
        cmd & 0xFF
    ]
    #print(f"Sending command: 0x{cmd:08X}")
    spi.xfer2(cmd_bytes)
    time.sleep(0.1)
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
